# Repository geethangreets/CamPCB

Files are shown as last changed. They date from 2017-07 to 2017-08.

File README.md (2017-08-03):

# Hardware Development of Illumination and Sensor Board for Multispectral Cameras System 
This project is about hardware development for a vital sign detection device

This is a device that allows patients to take images of wounds at their homes with a higher frequency compared to typical hospital visits. The images would then be made available to their clinicians for continuous wound monitoring.

System Diagram:
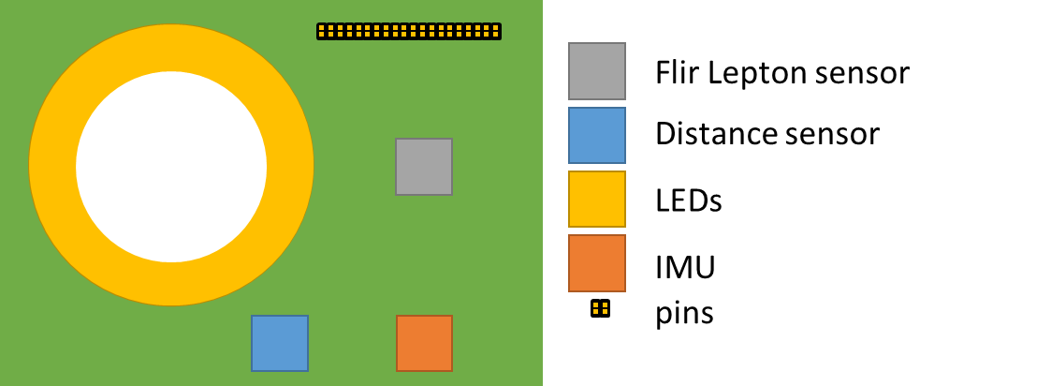
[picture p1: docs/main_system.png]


3D rendering of the assembly:
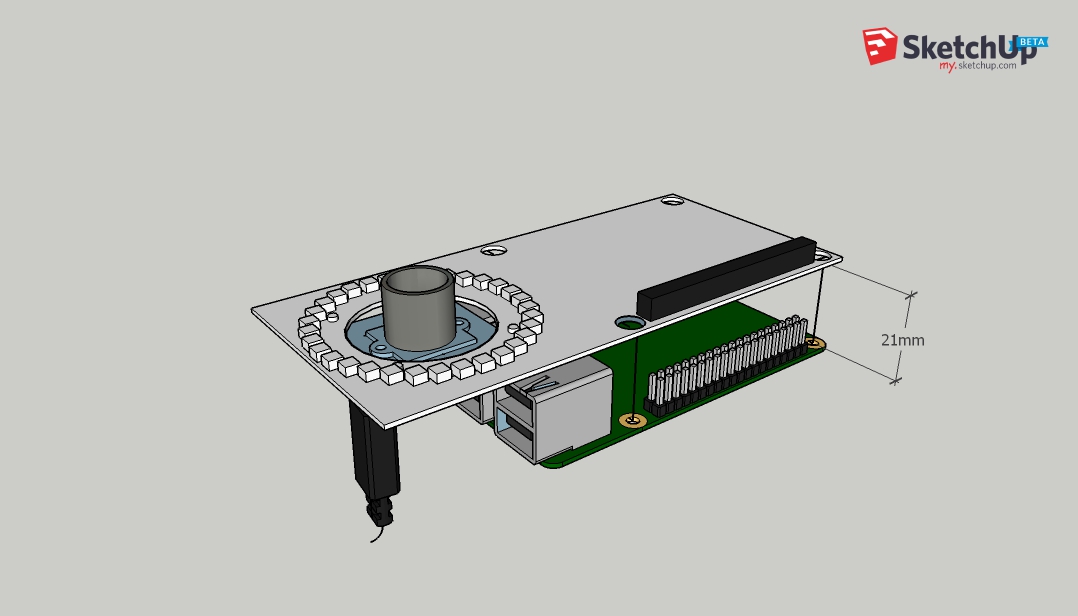
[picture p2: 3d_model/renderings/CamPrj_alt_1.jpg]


Final PCB rendering front and back
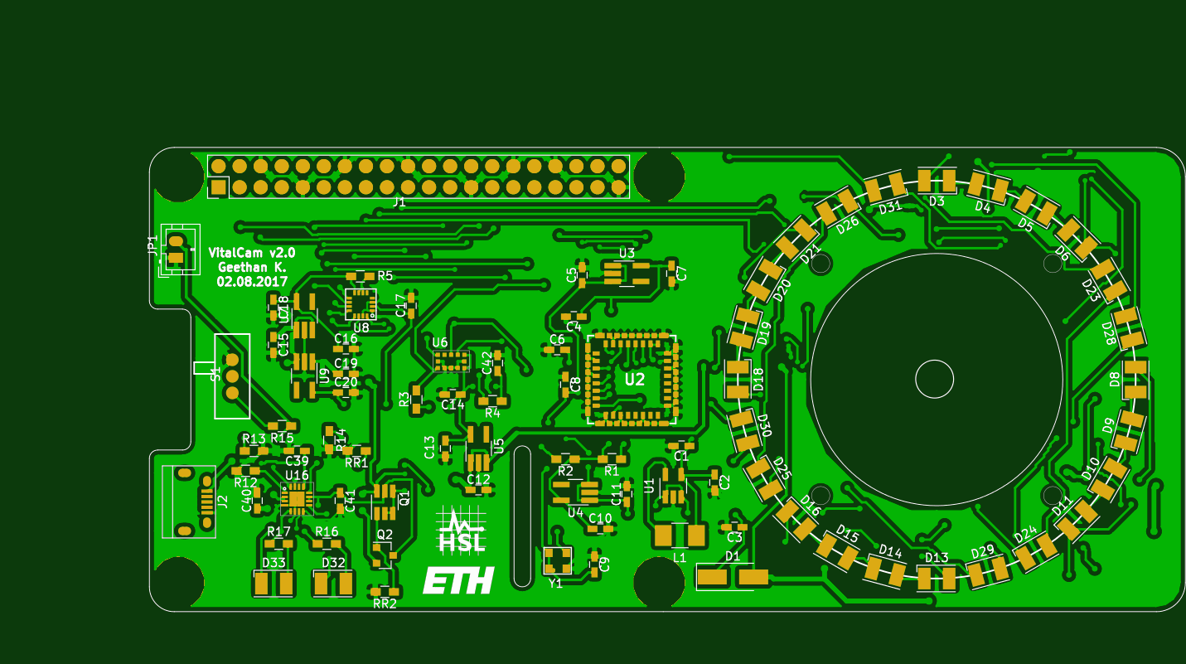
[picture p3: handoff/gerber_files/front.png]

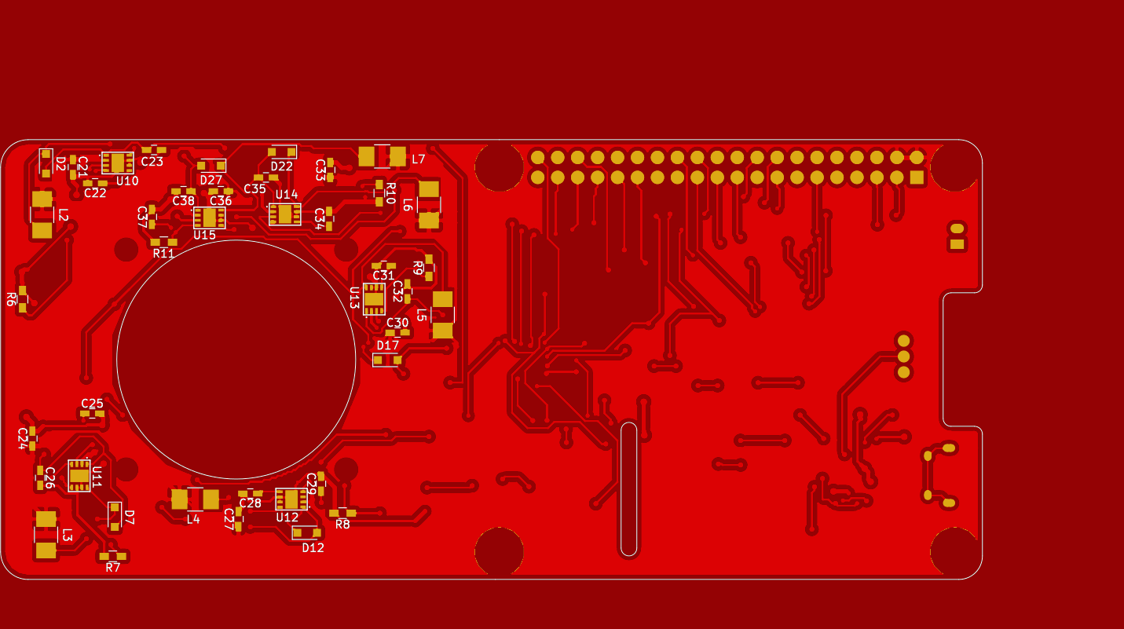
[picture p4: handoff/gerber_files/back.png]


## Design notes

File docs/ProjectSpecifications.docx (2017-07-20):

# Specifications Illumination and sensor board for multispectral cameras system

Author: Gaetano Scebba

Version: V3 (2017-06-02)

1. Motivation

Management and treatment of chronic wounds represent a challenge for both the patients and the medical practitioners. Typically, the wound healing process is slow, so the structural wound changes can be recognized only across several days or weeks. This is why most wound treatments involve weekly visits to the hospital, to document the current wound state. However, in some cases, this low frequency of hospital visits can lead to critical delays in wound interventions in case the wound condition changes more rapidly.

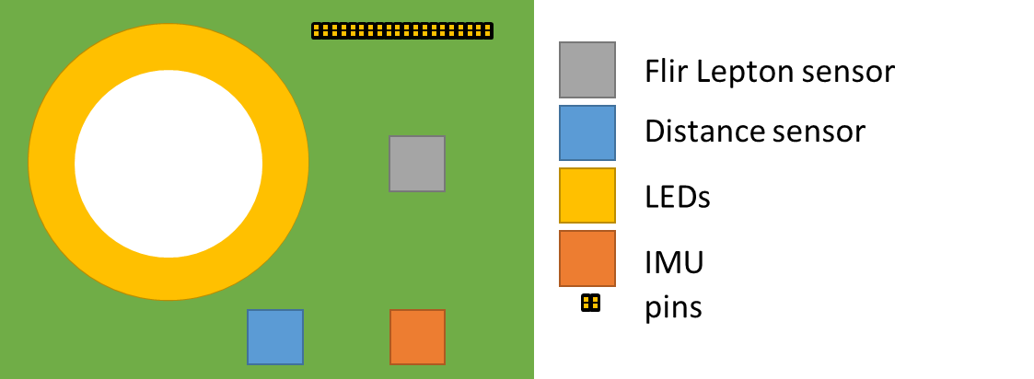
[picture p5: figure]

Our research group is interested in developing a device that allows patients to take images of wounds at their homes with a higher frequency compared to typical hospital visits. The images would then be made available to their clinicians for continuous wound monitoring.

Figure 1 Main components of the designed PCB

2. Purpose

The purpose of this document is to provide specifications for the design and develop of a printed circuit board (PCB) for enhancing a multispectral cameras system (VIS-IR econ systemse-CAM40_CUMI4682_MOD - 4 MP OV4682[^1]) interfaced to a Raspberry PI 3 board. The PCB (Figure 1) will provide following functions:

1. Illumination in infrared, ultraviolet and visible spectrum
2. Thermal (FIR) imaging
3. Distance measurement
4. Spatial orientation measurement
3. PCB specifications

Description | Quantity | Wavelength
SMD Infrared LED | 20 | 850 nm
SMD Ultra-violet LED | 4 | 405 nm
SMD White LED | 4 | -

- The PCB shall integrate the following sets of LEDs:
- The PCB shall integrate all the circuits and mounts for adding and operating the following sensors:
  - Flir Lepton infrared camera sensor;
  - ST’s VL53L0X distance sensor;
  - FIS1100 Inertial Measurement Unit;
- The PCB shall integrate 40 pins (2x20) to be interfaced with the Raspberry PI 3 board.
4. PCB requirements
- The intensity of each set of LEDs shall be individually controllable using continuous current;
- The Flir Lepton sensor shall be fully operational;
- The VL53L0X distance sensor shall be fully operational;

Figure 2 Format and dimensions

- The FIS1100 IMU shall be fully operational.

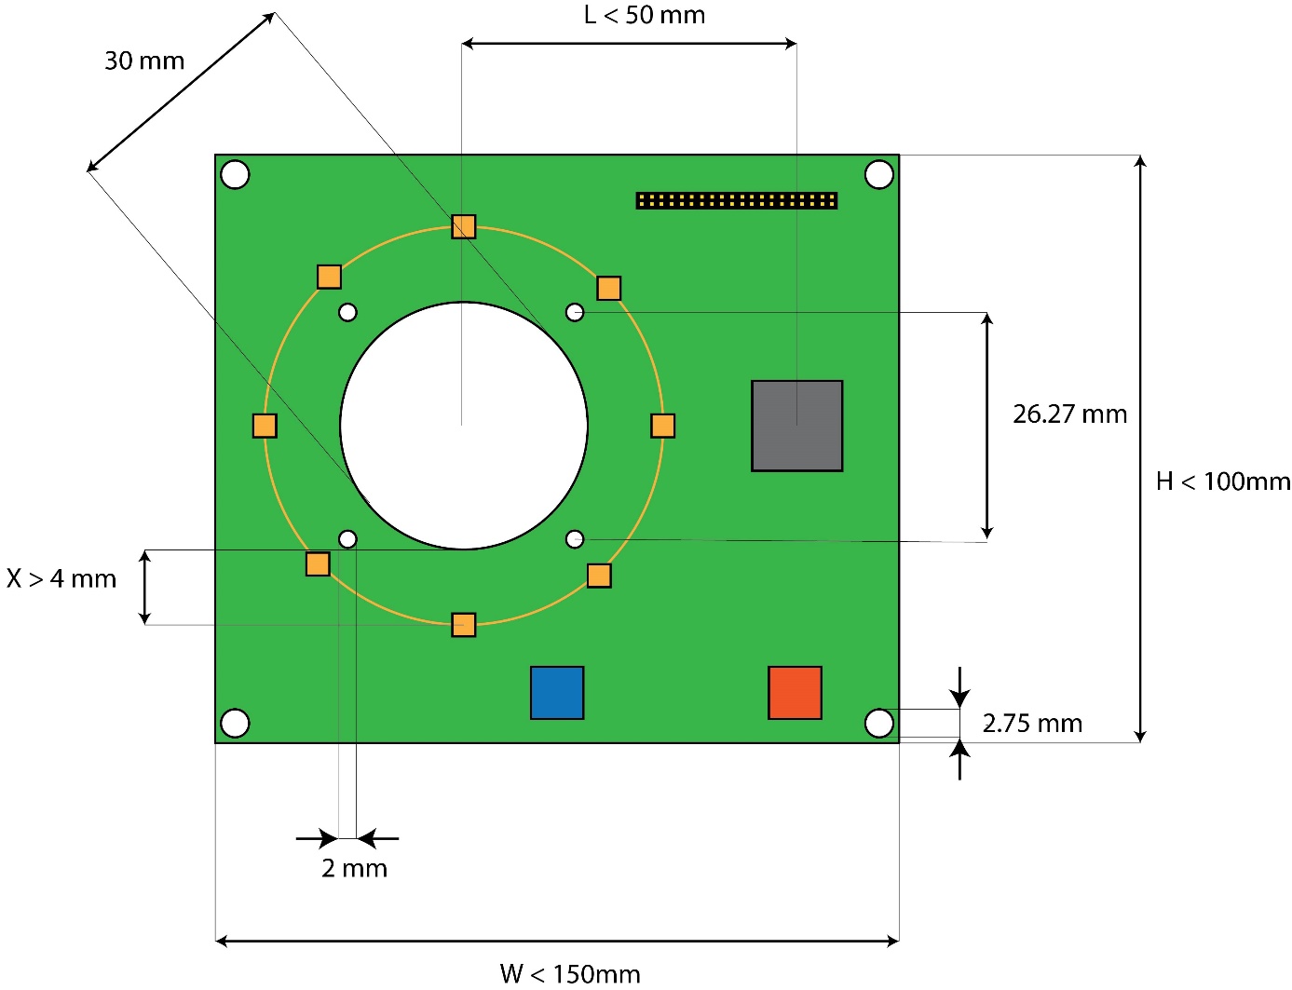
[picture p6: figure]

5. Tasks list
  5.1 Debug the existing PCB prototype;
  5.2 Design of the revised PCB with the desired specifications and requirements;
  5.3 Ordering of the components;
  5.4 PCB manufacturing;
  5.5 Test of the requirements;
  5.6 Documentation and getting-started guide.
6. Milestones
  6.1 Report of the bugs and planned revisions;
  6.2 Pre-manufacturing report of the PCB;
  6.3 Demo of the final system.
7. Further duties

Log worked hours and report weekly.

8. Components
  8.1 Flir Lepton sensor and breakout board

Figure 3 Flir Lepton sensor

Figure 4 Flir Lepton breakout board and Flir Lepton sensor

The Flir Lepton is an infrared camera system that integrates a fixed-focus lens assembly, an 80x60 long-wave infrared microbolometer sensor array, and the signal-processing electronics.

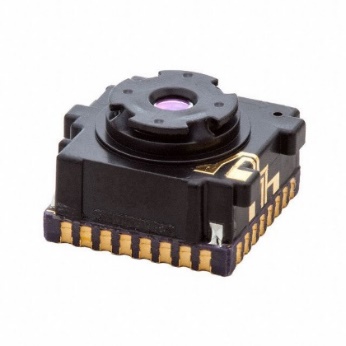
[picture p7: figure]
Image result for flir lepton sensor

The schematic of the operating circuit for the Flir Lepton is in FlirLeptonSensor/LeptonSchematic.pdf

8.2 VL53L0X Time-of Flight distance sensor carrier

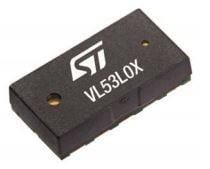
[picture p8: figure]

The VL53L0X is a time-of-flight laser sensor for distance measurement. It can measure absolute distances up to 2 meters.

Figure 4 VL53L0X distance sensor

The schematic of the operating circuit for the VL53L0X distance sensor is in DistanceSensor/DistSchematic.png

8.3 FIS1100 Inertial Measurement Unit

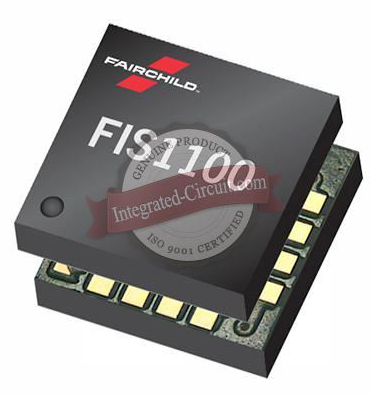
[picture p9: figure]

The FIS1100 is an integrated 6-axis MEMS sensor that includes a 3D accelerometer, a 3D gyroscope and a custom vector digital signal processor.

Figure 5 FIS1100 IMU

The datasheet of the FIS1100 IMU is in IMU/FIS1100Datasheet.pdf

[^1] https://www.e-consystems.com/OV4682-RGB-IR-MIPI-CAMERA-Module.asp

Specifications PCB camera extension board 4/4

Mobile Health Systems Lab

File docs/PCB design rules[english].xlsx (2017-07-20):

Sheet1
 | A | B | C | D
1 | SMS Design Rules (default) | Fat: Accepted by PCB pool (27.11.13) | 29.9.15, Michael Herold-Nadig
2
3 | What? | Values (mm) | Values (mil, obsolete)
4
5 | Minimum ring on Via | 0.2 mm all around | 8 mil all around
6 | Minimal Via (final diameter) | 0.3 mm hole / 0.7 mm pad | 12 mil hole / 28 mil pad | 0.2 mm / 8 mil hole for an extra charge
7 | Signal Via | 0.4 mm hole / 0.9 mm pad | 16 mil hole / 36 mil pad
8th | Larger Via 0.5 mm | 0.6 mm hole / 0.9 mm pad | 24 mil hole / 36 mil pad
9
10
11
12 | Minimum trace | 0.15 mm | 6 mil | 0.125 mm / 5 mil with surcharge
13 | Normal signal trace | 0.3 mm | 12 mils
14 | Normal supply line | 0.6 mm | 24 mil
15 | Main power supply conductor track | 1 mm | 40 mils
16
17
18 | Minimum clearance between conductors | 0.15 mm | 6 mil | 0.125 mm / 5 mil with surcharge
19 | Minimum clearance between hole & Cu | 0.3 mm | 12 mils | Can be guaranteed with a small restring on the inside of 0.15 mm around the circumference.
20 | Min. Distance to PCB outline | 0.2 mm | 8 mils
21
22 | The minimum font size in copper | 0.8 mm height, 0.15 mm line thickness, default font (Stroke) | 32 mil height, 6 mil thickness, default font (Stroke) | Bottom Layer = Mirror!
23 | Normal font size in copper | 1.5 mm height, 0.25 mm thickness, default font (stroke) | 60 mil height, 10 mil thickness, default font (Stroke) | Bottom Layer = Mirror!
24 | The minimum font size to Solder | 1.0 mm Height, 0.15 mm Thickness, Default Font (Stroke) | 40 m height | Under the writing, Cu surface (or even text in Cu) should be, so readable.
25 | Normal font size on Solder | 1.5 mm Height, 0.25 mm Thickness, Default Font (Stroke) | 60 m height | Under the writing, Cu surface (or even text in Cu) should be, so readable.
26
27
28
29
30 | paste mask | 100 μm thick (instead of 120 or 150 μm)
31 | Padreduktion, PasteMaskExpansion (especially with QFP important, otherwise too many shorts due to too much paste) | - 50 μm | - 2 mil

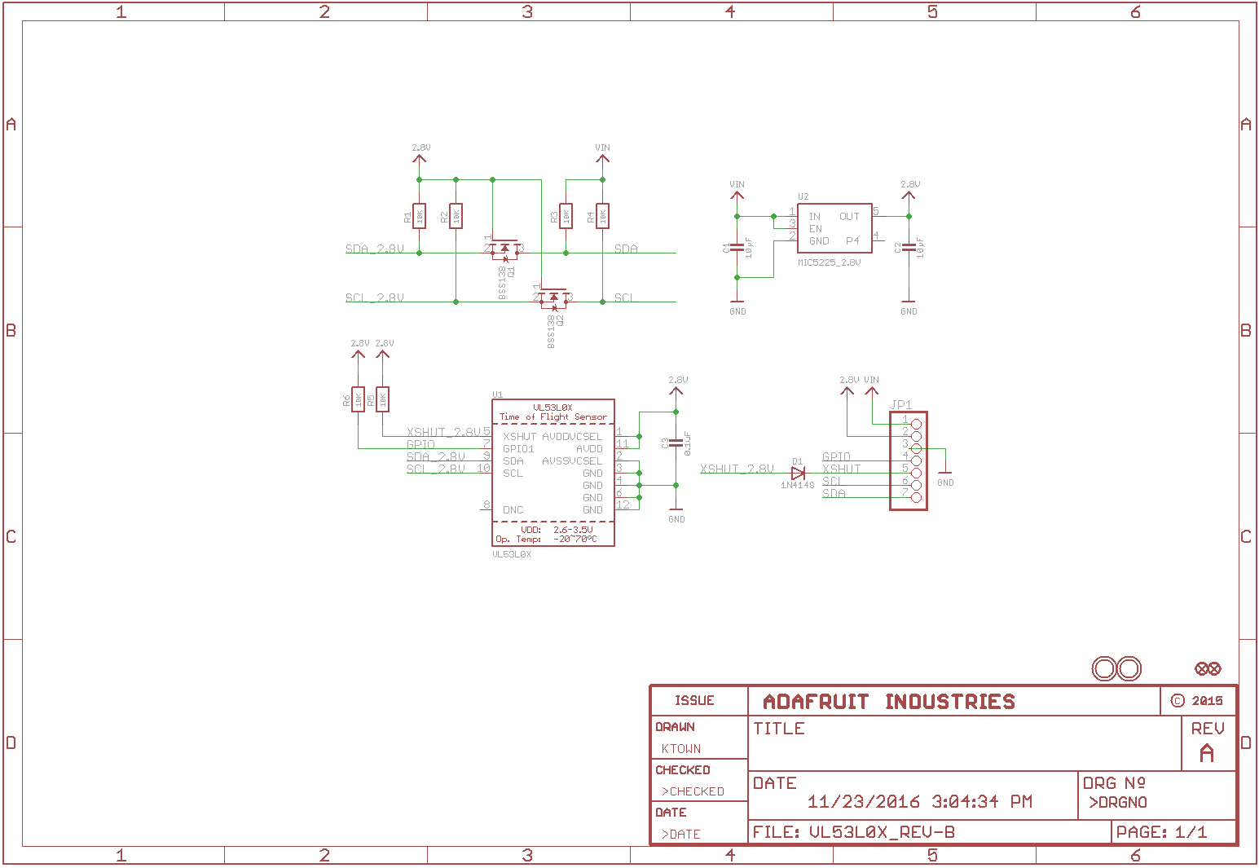
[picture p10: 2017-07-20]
DistanceSensor/DistSchematic.png

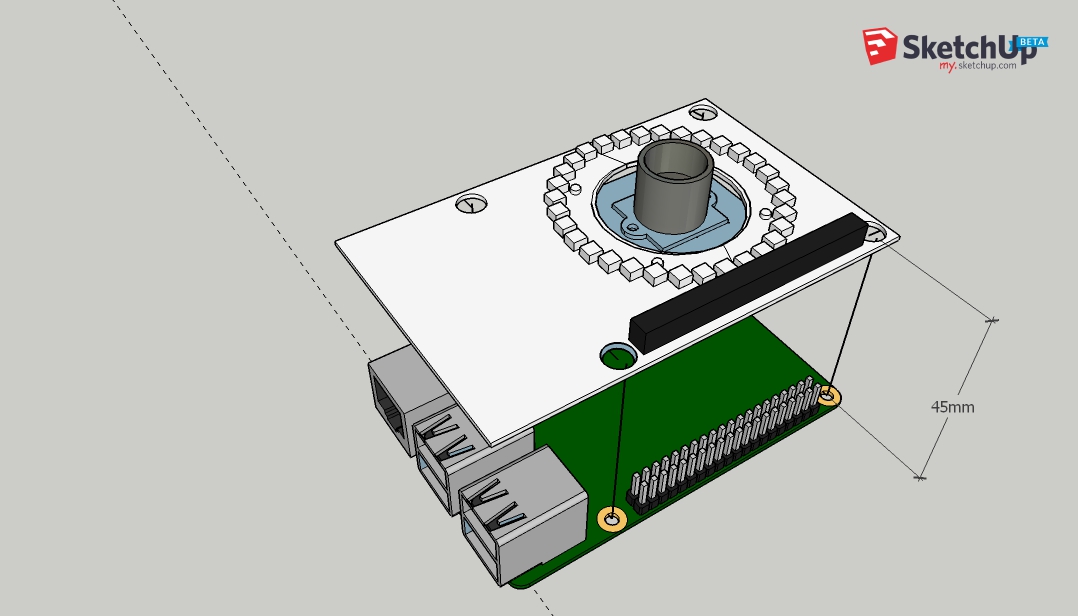
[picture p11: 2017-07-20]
3d_model/renderings/CamPrj_alt_2.jpg

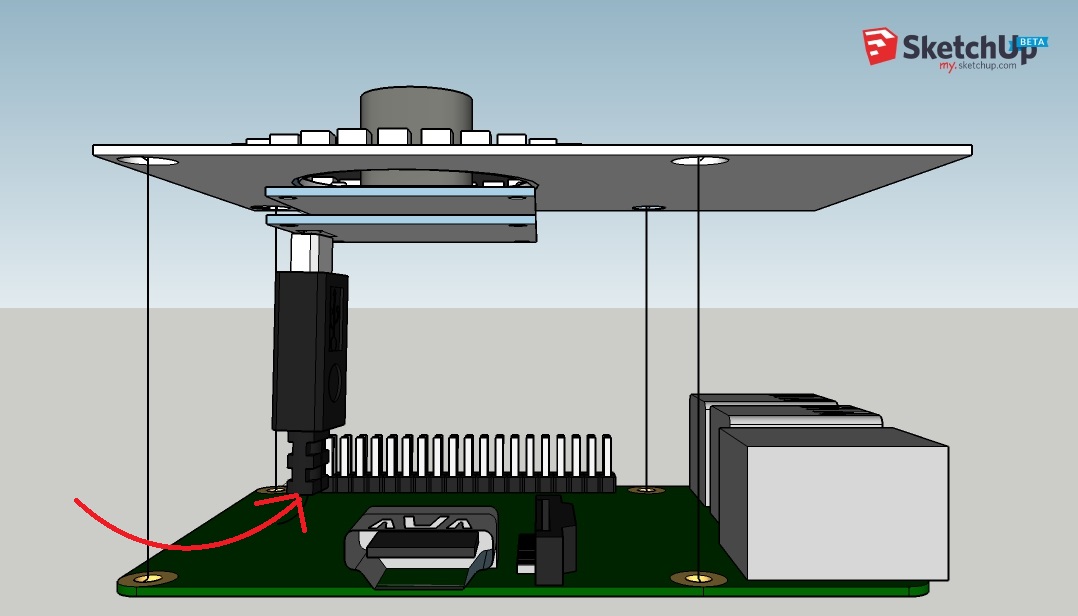
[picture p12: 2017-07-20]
3d_model/renderings/CamPrj_alt_2_access.jpg

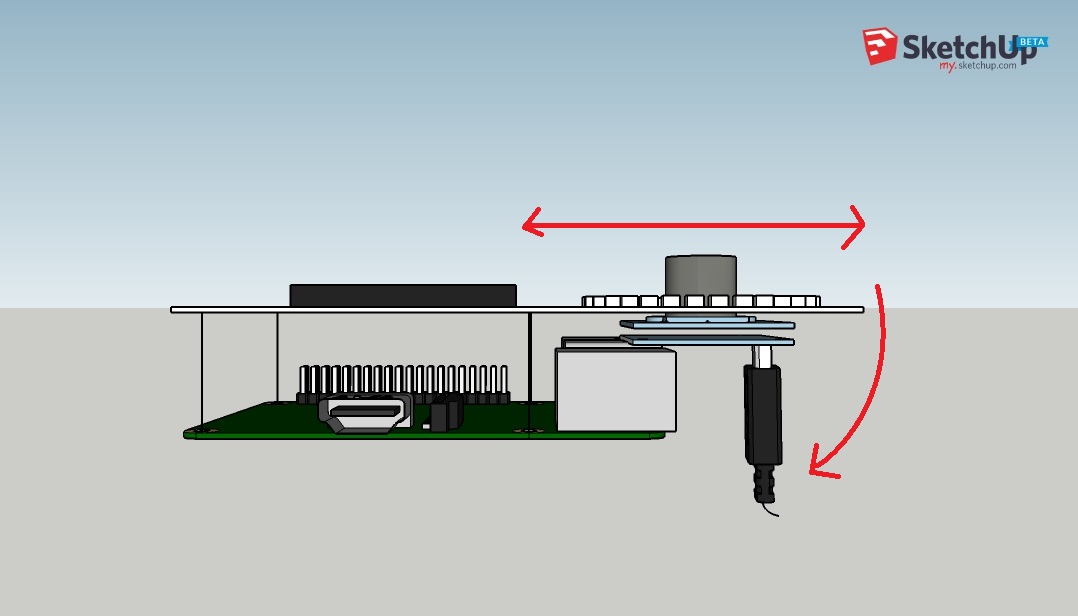
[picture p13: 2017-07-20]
3d_model/renderings/CamPrj_alt_1_stress.jpg

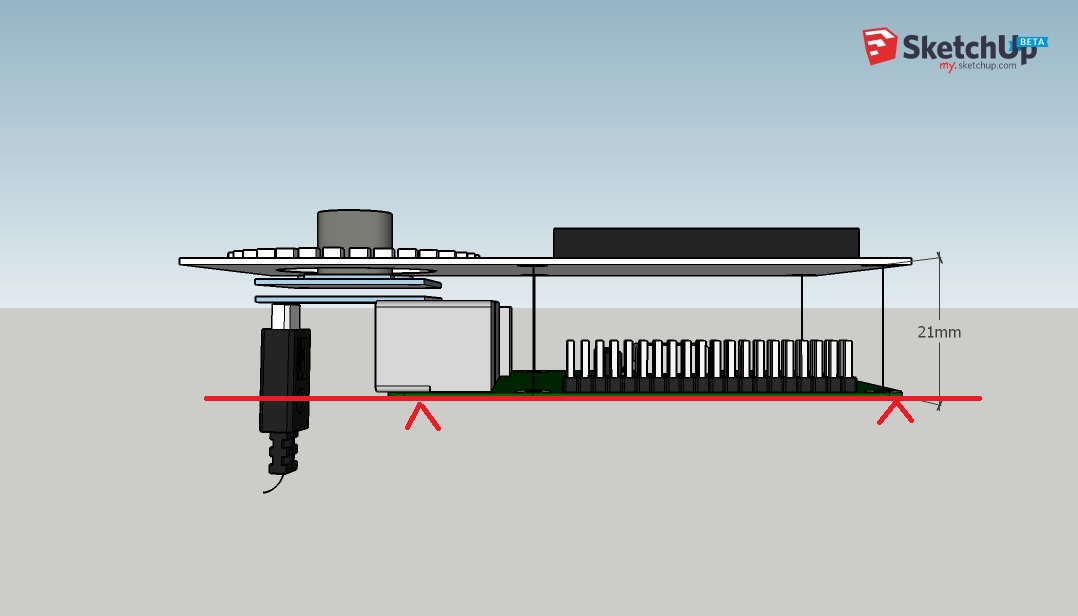
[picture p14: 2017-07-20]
3d_model/renderings/CamPrj_alt_1_usb_obs.jpg

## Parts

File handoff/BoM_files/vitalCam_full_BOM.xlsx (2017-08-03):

version | source | date | tool | number | name | tstamps | title | company | rev | date2 | source3 | number4 | value | ref | value5 | footprint | datasheet | field | name6 | lib | part | names | tstamps7 | tstamp | lib8 | part9 | description | fp | field10 | name11 | num | name12 | type | docs | logical | uri | code | name13 | ref14 | pin
D | E:/ETH/Summer2017/repo/camprj_kicad/camprj_kicad.sch | 8/2/2017 11:28:47 PM | Eeschema 4.0.6 | 1 | / | / |  |  |  | 15 nov 2012 | camprj_kicad.sch | 1
D | E:/ETH/Summer2017/repo/camprj_kicad/camprj_kicad.sch | 8/2/2017 11:28:47 PM | Eeschema 4.0.6 | 1 | / | / |  |  |  | 15 nov 2012 | camprj_kicad.sch | 2
D | E:/ETH/Summer2017/repo/camprj_kicad/camprj_kicad.sch | 8/2/2017 11:28:47 PM | Eeschema 4.0.6 | 1 | / | / |  |  |  | 15 nov 2012 | camprj_kicad.sch | 3
D | E:/ETH/Summer2017/repo/camprj_kicad/camprj_kicad.sch | 8/2/2017 11:28:47 PM | Eeschema 4.0.6 | 1 | / | / |  |  |  | 15 nov 2012 | camprj_kicad.sch | 4
D | E:/ETH/Summer2017/repo/camprj_kicad/camprj_kicad.sch | 8/2/2017 11:28:47 PM | Eeschema 4.0.6 | 2 | /RPI_pinout/ | /595CCA9D/ | Raspberry PI IO subcircuit | MHSL ETH Zurich | 1 | 2017-07-06 | RPI_pinout.sch | 1 | Geethan Karunaratne
D | E:/ETH/Summer2017/repo/camprj_kicad/camprj_kicad.sch | 8/2/2017 11:28:47 PM | Eeschema 4.0.6 | 2 | /RPI_pinout/ | /595CCA9D/ | Raspberry PI IO subcircuit | MHSL ETH Zurich | 1 | 2017-07-06 | RPI_pinout.sch | 2
D | E:/ETH/Summer2017/repo/camprj_kicad/camprj_kicad.sch | 8/2/2017 11:28:47 PM | Eeschema 4.0.6 | 2 | /RPI_pinout/ | /595CCA9D/ | Raspberry PI IO subcircuit | MHSL ETH Zurich | 1 | 2017-07-06 | RPI_pinout.sch | 3
D | E:/ETH/Summer2017/repo/camprj_kicad/camprj_kicad.sch | 8/2/2017 11:28:47 PM | Eeschema 4.0.6 | 2 | /RPI_pinout/ | /595CCA9D/ | Raspberry PI IO subcircuit | MHSL ETH Zurich | 1 | 2017-07-06 | RPI_pinout.sch | 4
D | E:/ETH/Summer2017/repo/camprj_kicad/camprj_kicad.sch | 8/2/2017 11:28:47 PM | Eeschema 4.0.6 | 3 | /thermal_sense/ | /595CCEDA/ | Termal sensor sub circuit | MHSL ETH Zurich | 1 | 2017-07-06 | thermal_sense.sch | 1 | Geethan Karunaratne
D | E:/ETH/Summer2017/repo/camprj_kicad/camprj_kicad.sch | 8/2/2017 11:28:47 PM | Eeschema 4.0.6 | 3 | /thermal_sense/ | /595CCEDA/ | Termal sensor sub circuit | MHSL ETH Zurich | 1 | 2017-07-06 | thermal_sense.sch | 2
D | E:/ETH/Summer2017/repo/camprj_kicad/camprj_kicad.sch | 8/2/2017 11:28:47 PM | Eeschema 4.0.6 | 3 | /thermal_sense/ | /595CCEDA/ | Termal sensor sub circuit | MHSL ETH Zurich | 1 | 2017-07-06 | thermal_sense.sch | 3
D | E:/ETH/Summer2017/repo/camprj_kicad/camprj_kicad.sch | 8/2/2017 11:28:47 PM | Eeschema 4.0.6 | 3 | /thermal_sense/ | /595CCEDA/ | Termal sensor sub circuit | MHSL ETH Zurich | 1 | 2017-07-06 | thermal_sense.sch | 4
D | E:/ETH/Summer2017/repo/camprj_kicad/camprj_kicad.sch | 8/2/2017 11:28:47 PM | Eeschema 4.0.6 | 4 | /dist_sensor/ | /595F7B59/ | Distance Sensor sub circuit | MHSL ETH Zurich | 1 | 2017-07-06 | dist_sensor.sch | 1 | Geethan Karunaratne
D | E:/ETH/Summer2017/repo/camprj_kicad/camprj_kicad.sch | 8/2/2017 11:28:47 PM | Eeschema 4.0.6 | 4 | /dist_sensor/ | /595F7B59/ | Distance Sensor sub circuit | MHSL ETH Zurich | 1 | 2017-07-06 | dist_sensor.sch | 2
D | E:/ETH/Summer2017/repo/camprj_kicad/camprj_kicad.sch | 8/2/2017 11:28:47 PM | Eeschema 4.0.6 | 4 | /dist_sensor/ | /595F7B59/ | Distance Sensor sub circuit | MHSL ETH Zurich | 1 | 2017-07-06 | dist_sensor.sch | 3
D | E:/ETH/Summer2017/repo/camprj_kicad/camprj_kicad.sch | 8/2/2017 11:28:47 PM | Eeschema 4.0.6 | 4 | /dist_sensor/ | /595F7B59/ | Distance Sensor sub circuit | MHSL ETH Zurich | 1 | 2017-07-06 | dist_sensor.sch | 4
D | E:/ETH/Summer2017/repo/camprj_kicad/camprj_kicad.sch | 8/2/2017 11:28:47 PM | Eeschema 4.0.6 | 5 | /IMU/ | /595FA242/ | IMU sub ciruit | MHSL ETH Zurich | 1 | 2017-07-06 | IMU.sch | 1 | Geethan Karunaratne
D | E:/ETH/Summer2017/repo/camprj_kicad/camprj_kicad.sch | 8/2/2017 11:28:47 PM | Eeschema 4.0.6 | 5 | /IMU/ | /595FA242/ | IMU sub ciruit | MHSL ETH Zurich | 1 | 2017-07-06 | IMU.sch | 2
D | E:/ETH/Summer2017/repo/camprj_kicad/camprj_kicad.sch | 8/2/2017 11:28:47 PM | Eeschema 4.0.6 | 5 | /IMU/ | /595FA242/ | IMU sub ciruit | MHSL ETH Zurich | 1 | 2017-07-06 | IMU.sch | 3
D | E:/ETH/Summer2017/repo/camprj_kicad/camprj_kicad.sch | 8/2/2017 11:28:47 PM | Eeschema 4.0.6 | 5 | /IMU/ | /595FA242/ | IMU sub ciruit | MHSL ETH Zurich | 1 | 2017-07-06 | IMU.sch | 4
D | E:/ETH/Summer2017/repo/camprj_kicad/camprj_kicad.sch | 8/2/2017 11:28:47 PM | Eeschema 4.0.6 | 6 | /LED_Drive/ | /59604F02/ |  |  |  |  | LED_Drive.sch | 1
D | E:/ETH/Summer2017/repo/camprj_kicad/camprj_kicad.sch | 8/2/2017 11:28:47 PM | Eeschema 4.0.6 | 6 | /LED_Drive/ | /59604F02/ |  |  |  |  | LED_Drive.sch | 2
D | E:/ETH/Summer2017/repo/camprj_kicad/camprj_kicad.sch | 8/2/2017 11:28:47 PM | Eeschema 4.0.6 | 6 | /LED_Drive/ | /59604F02/ |  |  |  |  | LED_Drive.sch | 3
D | E:/ETH/Summer2017/repo/camprj_kicad/camprj_kicad.sch | 8/2/2017 11:28:47 PM | Eeschema 4.0.6 | 6 | /LED_Drive/ | /59604F02/ |  |  |  |  | LED_Drive.sch | 4
D | E:/ETH/Summer2017/repo/camprj_kicad/camprj_kicad.sch | 8/2/2017 11:28:47 PM | Eeschema 4.0.6 | 7 | /LED_Drive/IR_SET1/ | /59604F02/59604F09/ | LED Driver | MHSL ETH Zurich | 1 | 2017-08-02 | single_led_drive.sch | 1 | Geethan Karunaratne
D | E:/ETH/Summer2017/repo/camprj_kicad/camprj_kicad.sch | 8/2/2017 11:28:47 PM | Eeschema 4.0.6 | 7 | /LED_Drive/IR_SET1/ | /59604F02/59604F09/ | LED Driver | MHSL ETH Zurich | 1 | 2017-08-02 | single_led_drive.sch | 2
D | E:/ETH/Summer2017/repo/camprj_kicad/camprj_kicad.sch | 8/2/2017 11:28:47 PM | Eeschema 4.0.6 | 7 | /LED_Drive/IR_SET1/ | /59604F02/59604F09/ | LED Driver | MHSL ETH Zurich | 1 | 2017-08-02 | single_led_drive.sch | 3
D | E:/ETH/Summer2017/repo/camprj_kicad/camprj_kicad.sch | 8/2/2017 11:28:47 PM | Eeschema 4.0.6 | 7 | /LED_Drive/IR_SET1/ | /59604F02/59604F09/ | LED Driver | MHSL ETH Zurich | 1 | 2017-08-02 | single_led_drive.sch | 4
D | E:/ETH/Summer2017/repo/camprj_kicad/camprj_kicad.sch | 8/2/2017 11:28:47 PM | Eeschema 4.0.6 | 8 | /LED_Drive/IR_SET2/ | /59604F02/59607CD4/ | LED Driver | MHSL ETH Zurich | 1 | 2017-08-02 | single_led_drive.sch | 1 | Geethan Karunaratne
D | E:/ETH/Summer2017/repo/camprj_kicad/camprj_kicad.sch | 8/2/2017 11:28:47 PM | Eeschema 4.0.6 | 8 | /LED_Drive/IR_SET2/ | /59604F02/59607CD4/ | LED Driver | MHSL ETH Zurich | 1 | 2017-08-02 | single_led_drive.sch | 2
D | E:/ETH/Summer2017/repo/camprj_kicad/camprj_kicad.sch | 8/2/2017 11:28:47 PM | Eeschema 4.0.6 | 8 | /LED_Drive/IR_SET2/ | /59604F02/59607CD4/ | LED Driver | MHSL ETH Zurich | 1 | 2017-08-02 | single_led_drive.sch | 3
D | E:/ETH/Summer2017/repo/camprj_kicad/camprj_kicad.sch | 8/2/2017 11:28:47 PM | Eeschema 4.0.6 | 8 | /LED_Drive/IR_SET2/ | /59604F02/59607CD4/ | LED Driver | MHSL ETH Zurich | 1 | 2017-08-02 | single_led_drive.sch | 4
D | E:/ETH/Summer2017/repo/camprj_kicad/camprj_kicad.sch | 8/2/2017 11:28:47 PM | Eeschema 4.0.6 | 9 | /LED_Drive/IR_SET3/ | /59604F02/5960845F/ | LED Driver | MHSL ETH Zurich | 1 | 2017-08-02 | single_led_drive.sch | 1 | Geethan Karunaratne
D | E:/ETH/Summer2017/repo/camprj_kicad/camprj_kicad.sch | 8/2/2017 11:28:47 PM | Eeschema 4.0.6 | 9 | /LED_Drive/IR_SET3/ | /59604F02/5960845F/ | LED Driver | MHSL ETH Zurich | 1 | 2017-08-02 | single_led_drive.sch | 2
D | E:/ETH/Summer2017/repo/camprj_kicad/camprj_kicad.sch | 8/2/2017 11:28:47 PM | Eeschema 4.0.6 | 9 | /LED_Drive/IR_SET3/ | /59604F02/5960845F/ | LED Driver | MHSL ETH Zurich | 1 | 2017-08-02 | single_led_drive.sch | 3
D | E:/ETH/Summer2017/repo/camprj_kicad/camprj_kicad.sch | 8/2/2017 11:28:47 PM | Eeschema 4.0.6 | 9 | /LED_Drive/IR_SET3/ | /59604F02/5960845F/ | LED Driver | MHSL ETH Zurich | 1 | 2017-08-02 | single_led_drive.sch | 4
D | E:/ETH/Summer2017/repo/camprj_kicad/camprj_kicad.sch | 8/2/2017 11:28:47 PM | Eeschema 4.0.6 | 10 | /LED_Drive/IR_SET4/ | /59604F02/59608613/ | LED Driver | MHSL ETH Zurich | 1 | 2017-08-02 | single_led_drive.sch | 1 | Geethan Karunaratne
D | E:/ETH/Summer2017/repo/camprj_kicad/camprj_kicad.sch | 8/2/2017 11:28:47 PM | Eeschema 4.0.6 | 10 | /LED_Drive/IR_SET4/ | /59604F02/59608613/ | LED Driver | MHSL ETH Zurich | 1 | 2017-08-02 | single_led_drive.sch | 2
D | E:/ETH/Summer2017/repo/camprj_kicad/camprj_kicad.sch | 8/2/2017 11:28:47 PM | Eeschema 4.0.6 | 10 | /LED_Drive/IR_SET4/ | /59604F02/59608613/ | LED Driver | MHSL ETH Zurich | 1 | 2017-08-02 | single_led_drive.sch | 3
D | E:/ETH/Summer2017/repo/camprj_kicad/camprj_kicad.sch | 8/2/2017 11:28:47 PM | Eeschema 4.0.6 | 10 | /LED_Drive/IR_SET4/ | /59604F02/59608613/ | LED Driver | MHSL ETH Zurich | 1 | 2017-08-02 | single_led_drive.sch | 4
D | E:/ETH/Summer2017/repo/camprj_kicad/camprj_kicad.sch | 8/2/2017 11:28:47 PM | Eeschema 4.0.6 | 11 | /LED_Drive/WH_SET1/ | /59604F02/59608776/ | LED Driver | MHSL ETH Zurich | 1 | 2017-08-02 | single_led_drive.sch | 1 | Geethan Karunaratne
D | E:/ETH/Summer2017/repo/camprj_kicad/camprj_kicad.sch | 8/2/2017 11:28:47 PM | Eeschema 4.0.6 | 11 | /LED_Drive/WH_SET1/ | /59604F02/59608776/ | LED Driver | MHSL ETH Zurich | 1 | 2017-08-02 | single_led_drive.sch | 2
D | E:/ETH/Summer2017/repo/camprj_kicad/camprj_kicad.sch | 8/2/2017 11:28:47 PM | Eeschema 4.0.6 | 11 | /LED_Drive/WH_SET1/ | /59604F02/59608776/ | LED Driver | MHSL ETH Zurich | 1 | 2017-08-02 | single_led_drive.sch | 3
D | E:/ETH/Summer2017/repo/camprj_kicad/camprj_kicad.sch | 8/2/2017 11:28:47 PM | Eeschema 4.0.6 | 11 | /LED_Drive/WH_SET1/ | /59604F02/59608776/ | LED Driver | MHSL ETH Zurich | 1 | 2017-08-02 | single_led_drive.sch | 4
D | E:/ETH/Summer2017/repo/camprj_kicad/camprj_kicad.sch | 8/2/2017 11:28:47 PM | Eeschema 4.0.6 | 12 | /LED_Drive/UV_SET1/ | /59604F02/59608870/ | LED Driver | MHSL ETH Zurich | 1 | 2017-08-02 | single_led_drive.sch | 1 | Geethan Karunaratne
D | E:/ETH/Summer2017/repo/camprj_kicad/camprj_kicad.sch | 8/2/2017 11:28:47 PM | Eeschema 4.0.6 | 12 | /LED_Drive/UV_SET1/ | /59604F02/59608870/ | LED Driver | MHSL ETH Zurich | 1 | 2017-08-02 | single_led_drive.sch | 2
D | E:/ETH/Summer2017/repo/camprj_kicad/camprj_kicad.sch | 8/2/2017 11:28:47 PM | Eeschema 4.0.6 | 12 | /LED_Drive/UV_SET1/ | /59604F02/59608870/ | LED Driver | MHSL ETH Zurich | 1 | 2017-08-02 | single_led_drive.sch | 3
D | E:/ETH/Summer2017/repo/camprj_kicad/camprj_kicad.sch | 8/2/2017 11:28:47 PM | Eeschema 4.0.6 | 12 | /LED_Drive/UV_SET1/ | /59604F02/59608870/ | LED Driver | MHSL ETH Zurich | 1 | 2017-08-02 | single_led_drive.sch | 4
D | E:/ETH/Summer2017/repo/camprj_kicad/camprj_kicad.sch | 8/2/2017 11:28:47 PM | Eeschema 4.0.6 | 13 | /power_supply/ | /595F39B0/ | USB charging and Power Supply | MHSL ETH Zurich | 1 | 2017-07-07 | power_supply.sch | 1 | Geethan Karunaratne
D | E:/ETH/Summer2017/repo/camprj_kicad/camprj_kicad.sch | 8/2/2017 11:28:47 PM | Eeschema 4.0.6 | 13 | /power_supply/ | /595F39B0/ | USB charging and Power Supply | MHSL ETH Zurich | 1 | 2017-07-07 | power_supply.sch | 2
D | E:/ETH/Summer2017/repo/camprj_kicad/camprj_kicad.sch | 8/2/2017 11:28:47 PM | Eeschema 4.0.6 | 13 | /power_supply/ | /595F39B0/ | USB charging and Power Supply | MHSL ETH Zurich | 1 | 2017-07-07 | power_supply.sch | 3
D | E:/ETH/Summer2017/repo/camprj_kicad/camprj_kicad.sch | 8/2/2017 11:28:47 PM | Eeschema 4.0.6 | 13 | /power_supply/ | /595F39B0/ | USB charging and Power Supply | MHSL ETH Zurich | 1 | 2017-07-07 | power_supply.sch | 4
D |  |  |  |  |  |  |  |  |  |  |  |  |  | J1 | 20x2 header | Pin_Headers:Pin_Header_Straight_2x20_Pitch2.54mm | http://suddendocs.samtec.com/catalog_english/esq_th.pdf | https://www.digikey.com/product-detail/en/ESQ-120-69-G-D-LL/ESQ-120-69-G-D-LL-ND/7098805?WT.z_cid=ref_neda_dkc_buynow | Buy Link | conn | Raspberry_Pi_2_3 | /RPI_pinout/ | /595CCA9D/ | 595CCB8C
D |  |  |  |  |  |  |  |  |  |  |  |  |  | J1 | 20x2 header | Pin_Headers:Pin_Header_Straight_2x20_Pitch2.54mm | http://suddendocs.samtec.com/catalog_english/esq_th.pdf | ESQ-120-69-G-D-LL | MPN | conn | Raspberry_Pi_2_3 | /RPI_pinout/ | /595CCA9D/ | 595CCB8C
D |  |  |  |  |  |  |  |  |  |  |  |  |  | U2 | Molex 1052028-1001 | Myfootprints:105028-1001 | http://www.mouser.com/ds/2/276/1050281001_OTHER_SOCKETS-152362.pdf | http://eu.mouser.com/ProductDetail/Molex/105028-1001/?qs=3OKVfsn1b5DSpyA99lGNjg%3D%3D | Buy Link | leptonBreakoutV4 | LEPTONCUSTOM_CAM-MODULE | /thermal_sense/ | /595CCEDA/ | 595DD16C
D |  |  |  |  |  |  |  |  |  |  |  |  |  | U2 | Molex 1052028-1001 | Myfootprints:105028-1001 | http://www.mouser.com/ds/2/276/1050281001_OTHER_SOCKETS-152362.pdf | 105028-1001 | MPN | leptonBreakoutV4 | LEPTONCUSTOM_CAM-MODULE | /thermal_sense/ | /595CCEDA/ | 595DD16C
D |  |  |  |  |  |  |  |  |  |  |  |  |  | U1 | LM3670SOT23-5 | TO_SOT_Packages_SMD:SOT-23-5_HandSoldering | http://www.ti.com/lit/ds/symlink/lm3670.pdf | http://eu.mouser.com/ProductDetail/Texas-Instruments/LM3670MFX-ADJ-NOPB/ | Buy Link | leptonBreakoutV4 | LEPTONCUSTOM_LM3670SOT23-5 | /thermal_sense/ | /595CCEDA/ | 595DD218
D |  |  |  |  |  |  |  |  |  |  |  |  |  | U1 | LM3670SOT23-5 | TO_SOT_Packages_SMD:SOT-23-5_HandSoldering | http://www.ti.com/lit/ds/symlink/lm3670.pdf | LM3670MFX-ADJ/NOPB | MPN | leptonBreakoutV4 | LEPTONCUSTOM_LM3670SOT23-5 | /thermal_sense/ | /595CCEDA/ | 595DD218
D |  |  |  |  |  |  |  |  |  |  |  |  |  | C1 | 10uF | Capacitors_SMD:C_0603_HandSoldering |  |  |  | device | C | /thermal_sense/ | /595CCEDA/ | 595DD448
D |  |  |  |  |  |  |  |  |  |  |  |  |  | L1 | 10uH | Inductors_SMD:L_1210_HandSoldering |  |  |  | device | L | /thermal_sense/ | /595CCEDA/ | 595DD4BD
D |  |  |  |  |  |  |  |  |  |  |  |  |  | C2 | 0.1uF | Capacitors_SMD:C_0603_HandSoldering |  |  |  | device | C | /thermal_sense/ | /595CCEDA/ | 595DD57E
D |  |  |  |  |  |  |  |  |  |  |  |  |  | Y1 | ASFLMB-25MHZ | Myfootprints:5X3.2-CRYSTAL | http://www.mouser.com/ds/2/3/ASFLMB-24525.pdf | http://eu.mouser.com/ProductDetail/ABRACON/ASFLMB-25000MHZ-LC-T/?qs=3YAjQa1E1OmYZx%252blyx8lOg%3D%3D | Buy Link | leptonBreakoutV4 | LEPTONCUSTOM_ASFLMB-25MHZ | /thermal_sense/ | /595CCEDA/ | 595DE58B
D |  |  |  |  |  |  |  |  |  |  |  |  |  | Y1 | ASFLMB-25MHZ | Myfootprints:5X3.2-CRYSTAL | http://www.mouser.com/ds/2/3/ASFLMB-24525.pdf | ASFLMB-25.000MHZ-LC-T | MPN | leptonBreakoutV4 | LEPTONCUSTOM_ASFLMB-25MHZ | /thermal_sense/ | /595CCEDA/ | 595DE58B
D |  |  |  |  |  |  |  |  |  |  |  |  |  | C9 | 10nF | Capacitors_SMD:C_0603_HandSoldering |  |  |  | device | C | /thermal_sense/ | /595CCEDA/ | 595DE822
D |  |  |  |  |  |  |  |  |  |  |  |  |  | R1 | 10K | Resistors_SMD:R_0603_HandSoldering |  |  |  | device | R | /thermal_sense/ | /595CCEDA/ | 595DEE4C
D |  |  |  |  |  |  |  |  |  |  |  |  |  | R2 | 100K | Resistors_SMD:R_0603_HandSoldering |  |  |  | device | R | /thermal_sense/ | /595CCEDA/ | 595DEEFC
D |  |  |  |  |  |  |  |  |  |  |  |  |  | C8 | 1uF | Capacitors_SMD:C_0603_HandSoldering |  |  |  | device | C | /thermal_sense/ | /595CCEDA/ | 595DFC4E
D |  |  |  |  |  |  |  |  |  |  |  |  |  | C6 | 0.1uF | Capacitors_SMD:C_0603_HandSoldering |  |  |  | device | C | /thermal_sense/ | /595CCEDA/ | 595DFD7F
D |  |  |  |  |  |  |  |  |  |  |  |  |  | U4 | ADP150AUJZ-2.8-R7 | TO_SOT_Packages_SMD:TSOT-23-5_HandSoldering | http://www.mouser.com/ds/2/609/ADP150-773560.pdf | http://eu.mouser.com/ProductDetail/Analog-Devices/ADP150AUJZ-28-R7/?qs=WIvQP4zGanh7WlpvNfrmXw%3D%3D | Buy Link | leptonBreakoutV4 | LEPTONCUSTOM_ADP150TSOT-5 | /thermal_sense/ | /595CCEDA/ | 595E0F8D
D |  |  |  |  |  |  |  |  |  |  |  |  |  | U4 | ADP150AUJZ-2.8-R7 | TO_SOT_Packages_SMD:TSOT-23-5_HandSoldering | http://www.mouser.com/ds/2/609/ADP150-773560.pdf | ADP150AUJZ-2.8-R7 | MPN | leptonBreakoutV4 | LEPTONCUSTOM_ADP150TSOT-5 | /thermal_sense/ | /595CCEDA/ | 595E0F8D
D |  |  |  |  |  |  |  |  |  |  |  |  |  | C10 | 1uF | Capacitors_SMD:C_0603_HandSoldering |  |  |  | device | C | /thermal_sense/ | /595CCEDA/ | 595E1253
D |  |  |  |  |  |  |  |  |  |  |  |  |  | C11 | 1uF | Capacitors_SMD:C_0603_HandSoldering |  |  |  | device | C | /thermal_sense/ | /595CCEDA/ | 595E224B
D |  |  |  |  |  |  |  |  |  |  |  |  |  | U3 | ADP150AUJZ-3.3-R7 | TO_SOT_Packages_SMD:TSOT-23-5_HandSoldering | http://www.mouser.com/ds/2/609/ADP150-773560.pdf | http://eu.mouser.com/ProductDetail/Analog-Devices/ADP150AUJZ-33-R7/?qs=WIvQP4zGanjNlX1MqHWsFA%3D%3D | Buy Link | leptonBreakoutV4 | LEPTONCUSTOM_ADP150TSOT-5 | /thermal_sense/ | /595CCEDA/ | 595E2ECE
D |  |  |  |  |  |  |  |  |  |  |  |  |  | U3 | ADP150AUJZ-3.3-R7 | TO_SOT_Packages_SMD:TSOT-23-5_HandSoldering | http://www.mouser.com/ds/2/609/ADP150-773560.pdf | ADP150AUJZ-3.3-R7 | MPN | leptonBreakoutV4 | LEPTONCUSTOM_ADP150TSOT-5 | /thermal_sense/ | /595CCEDA/ | 595E2ECE
D |  |  |  |  |  |  |  |  |  |  |  |  |  | C5 | 1uF | Capacitors_SMD:C_0603_HandSoldering |  |  |  | device | C | /thermal_sense/ | /595CCEDA/ | 595E31FF
D |  |  |  |  |  |  |  |  |  |  |  |  |  | C7 | 1uF | Capacitors_SMD:C_0603_HandSoldering |  |  |  | device | C | /thermal_sense/ | /595CCEDA/ | 595E3957
D |  |  |  |  |  |  |  |  |  |  |  |  |  | C4 | 0.1uF | Capacitors_SMD:C_0603_HandSoldering |  |  |  | device | C | /thermal_sense/ | /595CCEDA/ | 595E6083
D |  |  |  |  |  |  |  |  |  |  |  |  |  | C3 | 4.7uF | Capacitors_SMD:C_0603_HandSoldering |  |  |  | device | C | /thermal_sense/ | /595CCEDA/ | 595E8002
D |  |  |  |  |  |  |  |  |  |  |  |  |  | D1 | B340A | Myfootprints:D_SMA_Handsoldering_AC | http://www.mouser.com/ds/2/115/ds30891-89887.pdf | http://www.mouser.ch/ProductDetail/Diodes-Incorporated/B340A-13-F/?qs=aLaTXeBcTP9fj%2fYKVo6Q1A== | Buy Link | leptonBreakoutV4 | SCHOTTKY-B340A | /thermal_sense/ | /595CCEDA/ | 5974B1F1
D |  |  |  |  |  |  |  |  |  |  |  |  |  | D1 | B340A | Myfootprints:D_SMA_Handsoldering_AC | http://www.mouser.com/ds/2/115/ds30891-89887.pdf | B340A-13-F | MPN | leptonBreakoutV4 | SCHOTTKY-B340A | /thermal_sense/ | /595CCEDA/ | 5974B1F1
D |  |  |  |  |  |  |  |  |  |  |  |  |  | U6 | VL53L0X | Myfootprints:Optical_LGA12 | http://www.mouser.com/ds/2/389/en.DM00279086-952611.pdf | http://eu.mouser.com/ProductDetail/STMicroelectronics/VL53L0CXV0DH-1/?qs=dTJS0cRn7ojtsK3C9%252bTaSw%3d%3d | Buy Link | _sensors | VL53L0X | /dist_sensor/ | /595F7B59/ | 595F7B68
D |  |  |  |  |  |  |  |  |  |  |  |  |  | U6 | VL53L0X | Myfootprints:Optical_LGA12 | http://www.mouser.com/ds/2/389/en.DM00279086-952611.pdf | VL53L0CXV0DH/1 | MPN | _sensors | VL53L0X | /dist_sensor/ | /595F7B59/ | 595F7B68
D |  |  |  |  |  |  |  |  |  |  |  |  |  | R4 | 10K | Resistors_SMD:R_0603_HandSoldering |  |  |  | device | R | /dist_sensor/ | /595F7B59/ | 595F7CD2
D |  |  |  |  |  |  |  |  |  |  |  |  |  | R3 | 10K | Resistors_SMD:R_0603_HandSoldering |  |  |  | device | R | /dist_sensor/ | /595F7B59/ | 595F7D0D
D |  |  |  |  |  |  |  |  |  |  |  |  |  | U5 | ADP150AUJZ-3.3-R7 | TO_SOT_Packages_SMD:TSOT-23-5_HandSoldering | http://www.mouser.com/ds/2/609/ADP150-773560.pdf | http://eu.mouser.com/ProductDetail/Analog-Devices/ADP150AUJZ-33-R7/?qs=WIvQP4zGanjNlX1MqHWsFA%3D%3D | Buy Link | leptonBreakoutV4 | LEPTONCUSTOM_ADP150TSOT-5 | /dist_sensor/ | /595F7B59/ | 595F8383
D |  |  |  |  |  |  |  |  |  |  |  |  |  | U5 | ADP150AUJZ-3.3-R7 | TO_SOT_Packages_SMD:TSOT-23-5_HandSoldering | http://www.mouser.com/ds/2/609/ADP150-773560.pdf | ADP150AUJZ-3.3-R7 | MPN | leptonBreakoutV4 | LEPTONCUSTOM_ADP150TSOT-5 | /dist_sensor/ | /595F7B59/ | 595F8383
D |  |  |  |  |  |  |  |  |  |  |  |  |  | C13 | 10uF | Capacitors_SMD:C_0603_HandSoldering |  |  |  | device | C | /dist_sensor/ | /595F7B59/ | 595F879F
D |  |  |  |  |  |  |  |  |  |  |  |  |  | C12 | 10uF | Capacitors_SMD:C_0603_HandSoldering |  |  |  | device | C | /dist_sensor/ | /595F7B59/ | 595F8DF4
D |  |  |  |  |  |  |  |  |  |  |  |  |  | C14 | 4.7u | Capacitors_SMD:C_0603_HandSoldering |  |  |  | device | C | /dist_sensor/ | /595F7B59/ | 595F9601
D |  |  |  |  |  |  |  |  |  |  |  |  |  | C42 | 100n | Capacitors_SMD:C_0603_HandSoldering |  |  |  | device | C | /dist_sensor/ | /595F7B59/ | 59657C20
D |  |  |  |  |  |  |  |  |  |  |  |  |  | U8 | FIS1100 | Myfootprints:LGA16 | http://www.mouser.com/ds/2/308/FIS1100-1119815.pdf | http://eu.mouser.com/ProductDetail/Fairchild-Semiconductor/FIS1100/?qs=Pve5fMu%2FDEuZUDX%2Fo6J%252b1g%3D%3D | Buy Link | mynew_lib | FIS1100 | /IMU/ | /595FA242/ | 595FAAF9
D |  |  |  |  |  |  |  |  |  |  |  |  |  | U8 | FIS1100 | Myfootprints:LGA16 | http://www.mouser.com/ds/2/308/FIS1100-1119815.pdf | FIS1100 | MPN | mynew_lib | FIS1100 | /IMU/ | /595FA242/ | 595FAAF9
D |  |  |  |  |  |  |  |  |  |  |  |  |  | C16 | 100nF | Capacitors_SMD:C_0603_HandSoldering |  |  |  | device | C | /IMU/ | /595FA242/ | 595FABCD
D |  |  |  |  |  |  |  |  |  |  |  |  |  | U7 | ADP150AUJZ-3.3-R7 | TO_SOT_Packages_SMD:TSOT-23-5_HandSoldering | http://www.mouser.com/ds/2/609/ADP150-773560.pdf | http://eu.mouser.com/ProductDetail/Analog-Devices/ADP150AUJZ-33-R7/?qs=WIvQP4zGanjNlX1MqHWsFA%3D%3D | Buy Link | leptonBreakoutV4 | LEPTONCUSTOM_ADP150TSOT-5 | /IMU/ | /595FA242/ | 595FC827
D |  |  |  |  |  |  |  |  |  |  |  |  |  | U7 | ADP150AUJZ-3.3-R7 | TO_SOT_Packages_SMD:TSOT-23-5_HandSoldering | http://www.mouser.com/ds/2/609/ADP150-773560.pdf | ADP150AUJZ-3.3-R7 | MPN | leptonBreakoutV4 | LEPTONCUSTOM_ADP150TSOT-5 | /IMU/ | /595FA242/ | 595FC827
D |  |  |  |  |  |  |  |  |  |  |  |  |  | C15 | 1uF | Capacitors_SMD:C_0603_HandSoldering |  |  |  | device | C | /IMU/ | /595FA242/ | 595FC82E
D |  |  |  |  |  |  |  |  |  |  |  |  |  | C18 | 1uF | Capacitors_SMD:C_0603_HandSoldering |  |  |  | device | C | /IMU/ | /595FA242/ | 595FC83B
D |  |  |  |  |  |  |  |  |  |  |  |  |  | U9 | ADP150AUJZ-1.8-R7 | TO_SOT_Packages_SMD:TSOT-23-5_HandSoldering | http://www.mouser.com/ds/2/609/ADP150-773560.pdf | http://eu.mouser.com/ProductDetail/Analog-Devices/ADP150AUJZ-18-R7/?qs=WIvQP4zGanj6me7Xqf%252bL8w%3D%3D | Buy Link | leptonBreakoutV4 | LEPTONCUSTOM_ADP150TSOT-5 | /IMU/ | /595FA242/ | 595FCBB7
D |  |  |  |  |  |  |  |  |  |  |  |  |  | U9 | ADP150AUJZ-1.8-R7 | TO_SOT_Packages_SMD:TSOT-23-5_HandSoldering | http://www.mouser.com/ds/2/609/ADP150-773560.pdf | ADP150AUJZ-1.8-R7 | MPN | leptonBreakoutV4 | LEPTONCUSTOM_ADP150TSOT-5 | /IMU/ | /595FA242/ | 595FCBB7
D |  |  |  |  |  |  |  |  |  |  |  |  |  | C19 | 1uF | Capacitors_SMD:C_0603_HandSoldering |  |  |  | device | C | /IMU/ | /595FA242/ | 595FCBBE
D |  |  |  |  |  |  |  |  |  |  |  |  |  | C20 | 1uF | Capacitors_SMD:C_0603_HandSoldering |  |  |  | device | C | /IMU/ | /595FA242/ | 595FCBCB
D |  |  |  |  |  |  |  |  |  |  |  |  |  | C17 | 100nF | Capacitors_SMD:C_0603_HandSoldering |  |  |  | device | C | /IMU/ | /595FA242/ | 595FD69A
D |  |  |  |  |  |  |  |  |  |  |  |  |  | R5 | 10K | Resistors_SMD:R_0603_HandSoldering |  |  |  | device | R | /IMU/ | /595FA242/ | 595FE3A0
D |  |  |  |  |  |  |  |  |  |  |  |  |  | U10 | MAX1561 | SparkFun-PowerIC:8-TDFN-EP | http://www.mouser.com/ds/2/256/MAX1561-MAX1599-65829.pdf | http://www.mouser.ch/ProductDetail/Maxim-Integrated/MAX1561ETA+T/?qs=p6VZ%252bklCkRSw1RT%2f%2fPr34Q== | Buy Link | MAX1599 | MAX1599 | /LED_Drive/IR_SET1/ | /59604F02/59604F09/ | 59604F14
D |  |  |  |  |  |  |  |  |  |  |  |  |  | U10 | MAX1561 | SparkFun-PowerIC:8-TDFN-EP | http://www.mouser.com/ds/2/256/MAX1561-MAX1599-65829.pdf | MAX1561ETA+T | MPN | MAX1599 | MAX1599 | /LED_Drive/IR_SET1/ | /59604F02/59604F09/ | 59604F14
D |  |  |  |  |  |  |  |  |  |  |  |  |  | C22 | 0.1uF | Capacitors_SMD:C_0603_HandSoldering |  |  |  | device | C | /LED_Drive/IR_SET1/ | /59604F02/59604F09/ | 5960555F
D |  |  |  |  |  |  |  |  |  |  |  |  |  | C21 | 2.2uF | Capacitors_SMD:C_0603_HandSoldering |  |  |  | device | C | /LED_Drive/IR_SET1/ | /59604F02/59604F09/ | 5960566F
D |  |  |  |  |  |  |  |  |  |  |  |  |  | C23 | 0.1uF | Capacitors_SMD:C_0603_HandSoldering |  |  |  | device | C | /LED_Drive/IR_SET1/ | /59604F02/59604F09/ | 5960587B
D |  |  |  |  |  |  |  |  |  |  |  |  |  | L2 | 47uH | Inductors_SMD:L_1210_HandSoldering |  |  |  | device | L | /LED_Drive/IR_SET1/ | /59604F02/59604F09/ | 59605DEA
D |  |  |  |  |  |  |  |  |  |  |  |  |  | D3 | LED | LEDs:LED_PLCC-2 |  |  |  | device | LED | /LED_Drive/IR_SET1/ | /59604F02/59604F09/ | 59606309
D |  |  |  |  |  |  |  |  |  |  |  |  |  | D4 | LED | LEDs:LED_PLCC-2 |  |  |  | device | LED | /LED_Drive/IR_SET1/ | /59604F02/59604F09/ | 596063DB
D |  |  |  |  |  |  |  |  |  |  |  |  |  | D5 | LED | LEDs:LED_PLCC-2 |  |  |  | device | LED | /LED_Drive/IR_SET1/ | /59604F02/59604F09/ | 596064A1
D |  |  |  |  |  |  |  |  |  |  |  |  |  | D6 | LED | LEDs:LED_PLCC-2 |  |  |  | device | LED | /LED_Drive/IR_SET1/ | /59604F02/59604F09/ | 596064D7
D |  |  |  |  |  |  |  |  |  |  |  |  |  | R6 | 7.5 | Resistors_SMD:R_0603_HandSoldering |  |  |  | device | R | /LED_Drive/IR_SET1/ | /59604F02/59604F09/ | 59606544
D |  |  |  |  |  |  |  |  |  |  |  |  |  | D2 | CMDSH2-3 | Diodes_SMD:D_SOD-323_HandSoldering | http://www.mouser.com/ds/2/68/cmdsh2-3-39086.pdf | http://www.mouser.ch/ProductDetail/Central-Semiconductor/CMDSH2-3-TR/?qs=AjE1biBnhWMUdOF9vZ5x%252bg== | Buy Link | mynew_lib | CMDSH2-3 | /LED_Drive/IR_SET1/ | /59604F02/59604F09/ | 597479DB
D |  |  |  |  |  |  |  |  |  |  |  |  |  | D2 | CMDSH2-3 | Diodes_SMD:D_SOD-323_HandSoldering | http://www.mouser.com/ds/2/68/cmdsh2-3-39086.pdf | CMDSH2-3 TR | MPN | mynew_lib | CMDSH2-3 | /LED_Drive/IR_SET1/ | /59604F02/59604F09/ | 597479DB
D |  |  |  |  |  |  |  |  |  |  |  |  |  | U11 | MAX1561 | SparkFun-PowerIC:8-TDFN-EP | http://www.mouser.com/ds/2/256/MAX1561-MAX1599-65829.pdf | http://www.mouser.ch/ProductDetail/Maxim-Integrated/MAX1561ETA+T/?qs=p6VZ%252bklCkRSw1RT%2f%2fPr34Q== | Buy Link | MAX1599 | MAX1599 | /LED_Drive/IR_SET2/ | /59604F02/59607CD4/ | 59604F14
D |  |  |  |  |  |  |  |  |  |  |  |  |  | U11 | MAX1561 | SparkFun-PowerIC:8-TDFN-EP | http://www.mouser.com/ds/2/256/MAX1561-MAX1599-65829.pdf | MAX1561ETA+T | MPN | MAX1599 | MAX1599 | /LED_Drive/IR_SET2/ | /59604F02/59607CD4/ | 59604F14
D |  |  |  |  |  |  |  |  |  |  |  |  |  | C25 | 0.1uF | Capacitors_SMD:C_0603_HandSoldering |  |  |  | device | C | /LED_Drive/IR_SET2/ | /59604F02/59607CD4/ | 5960555F
D |  |  |  |  |  |  |  |  |  |  |  |  |  | C24 | 2.2uF | Capacitors_SMD:C_0603_HandSoldering |  |  |  | device | C | /LED_Drive/IR_SET2/ | /59604F02/59607CD4/ | 5960566F
D |  |  |  |  |  |  |  |  |  |  |  |  |  | C26 | 0.1uF | Capacitors_SMD:C_0603_HandSoldering |  |  |  | device | C | /LED_Drive/IR_SET2/ | /59604F02/59607CD4/ | 5960587B
D |  |  |  |  |  |  |  |  |  |  |  |  |  | L3 | 47uH | Inductors_SMD:L_1210_HandSoldering |  |  |  | device | L | /LED_Drive/IR_SET2/ | /59604F02/59607CD4/ | 59605DEA
D |  |  |  |  |  |  |  |  |  |  |  |  |  | D8 | LED | LEDs:LED_PLCC-2 |  |  |  | device | LED | /LED_Drive/IR_SET2/ | /59604F02/59607CD4/ | 59606309
D |  |  |  |  |  |  |  |  |  |  |  |  |  | D9 | LED | LEDs:LED_PLCC-2 |  |  |  | device | LED | /LED_Drive/IR_SET2/ | /59604F02/59607CD4/ | 596063DB
D |  |  |  |  |  |  |  |  |  |  |  |  |  | D10 | LED | LEDs:LED_PLCC-2 |  |  |  | device | LED | /LED_Drive/IR_SET2/ | /59604F02/59607CD4/ | 596064A1
D |  |  |  |  |  |  |  |  |  |  |  |  |  | D11 | LED | LEDs:LED_PLCC-2 |  |  |  | device | LED | /LED_Drive/IR_SET2/ | /59604F02/59607CD4/ | 596064D7
D |  |  |  |  |  |  |  |  |  |  |  |  |  | R7 | 7.5 | Resistors_SMD:R_0603_HandSoldering |  |  |  | device | R | /LED_Drive/IR_SET2/ | /59604F02/59607CD4/ | 59606544
D |  |  |  |  |  |  |  |  |  |  |  |  |  | D7 | CMDSH2-3 | Diodes_SMD:D_SOD-323_HandSoldering | http://www.mouser.com/ds/2/68/cmdsh2-3-39086.pdf | http://www.mouser.ch/ProductDetail/Central-Semiconductor/CMDSH2-3-TR/?qs=AjE1biBnhWMUdOF9vZ5x%252bg== | Buy Link | mynew_lib | CMDSH2-3 | /LED_Drive/IR_SET2/ | /59604F02/59607CD4/ | 597479DB
D |  |  |  |  |  |  |  |  |  |  |  |  |  | D7 | CMDSH2-3 | Diodes_SMD:D_SOD-323_HandSoldering | http://www.mouser.com/ds/2/68/cmdsh2-3-39086.pdf | CMDSH2-3 TR | MPN | mynew_lib | CMDSH2-3 | /LED_Drive/IR_SET2/ | /59604F02/59607CD4/ | 597479DB
D |  |  |  |  |  |  |  |  |  |  |  |  |  | U12 | MAX1561 | SparkFun-PowerIC:8-TDFN-EP | http://www.mouser.com/ds/2/256/MAX1561-MAX1599-65829.pdf | http://www.mouser.ch/ProductDetail/Maxim-Integrated/MAX1561ETA+T/?qs=p6VZ%252bklCkRSw1RT%2f%2fPr34Q== | Buy Link | MAX1599 | MAX1599 | /LED_Drive/IR_SET3/ | /59604F02/5960845F/ | 59604F14
D |  |  |  |  |  |  |  |  |  |  |  |  |  | U12 | MAX1561 | SparkFun-PowerIC:8-TDFN-EP | http://www.mouser.com/ds/2/256/MAX1561-MAX1599-65829.pdf | MAX1561ETA+T | MPN | MAX1599 | MAX1599 | /LED_Drive/IR_SET3/ | /59604F02/5960845F/ | 59604F14
D |  |  |  |  |  |  |  |  |  |  |  |  |  | C28 | 0.1uF | Capacitors_SMD:C_0603_HandSoldering |  |  |  | device | C | /LED_Drive/IR_SET3/ | /59604F02/5960845F/ | 5960555F
D |  |  |  |  |  |  |  |  |  |  |  |  |  | C27 | 2.2uF | Capacitors_SMD:C_0603_HandSoldering |  |  |  | device | C | /LED_Drive/IR_SET3/ | /59604F02/5960845F/ | 5960566F
D |  |  |  |  |  |  |  |  |  |  |  |  |  | C29 | 0.1uF | Capacitors_SMD:C_0603_HandSoldering |  |  |  | device | C | /LED_Drive/IR_SET3/ | /59604F02/5960845F/ | 5960587B
D |  |  |  |  |  |  |  |  |  |  |  |  |  | L4 | 47uH | Inductors_SMD:L_1210_HandSoldering |  |  |  | device | L | /LED_Drive/IR_SET3/ | /59604F02/5960845F/ | 59605DEA
D |  |  |  |  |  |  |  |  |  |  |  |  |  | D13 | LED | LEDs:LED_PLCC-2 |  |  |  | device | LED | /LED_Drive/IR_SET3/ | /59604F02/5960845F/ | 59606309
D |  |  |  |  |  |  |  |  |  |  |  |  |  | D14 | LED | LEDs:LED_PLCC-2 |  |  |  | device | LED | /LED_Drive/IR_SET3/ | /59604F02/5960845F/ | 596063DB
D |  |  |  |  |  |  |  |  |  |  |  |  |  | D15 | LED | LEDs:LED_PLCC-2 |  |  |  | device | LED | /LED_Drive/IR_SET3/ | /59604F02/5960845F/ | 596064A1
D |  |  |  |  |  |  |  |  |  |  |  |  |  | D16 | LED | LEDs:LED_PLCC-2 |  |  |  | device | LED | /LED_Drive/IR_SET3/ | /59604F02/5960845F/ | 596064D7
D |  |  |  |  |  |  |  |  |  |  |  |  |  | R8 | 7.5 | Resistors_SMD:R_0603_HandSoldering |  |  |  | device | R | /LED_Drive/IR_SET3/ | /59604F02/5960845F/ | 59606544
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

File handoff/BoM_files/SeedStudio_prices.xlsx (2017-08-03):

Component provider | Designator | MPN | SeeedSKU | Description | Quantity | Unit Price | Amount
Seeed | U2 | 105028-1001 | 508000001 | IC 及元件插座 8.5*8.5 AUTO FOCUS C AMERA SOCKET ASSY | 1 * 5 | 2.1026 | 10.513
Seeed | U1 | LM3670MFX-ADJ/NOPB | 508000001 | 轉換電壓穩壓器 Miniature Step-Down DC-DC Converter for Ultra Low Voltage Circuits 5-SOT-23 -40 to 85 | 1 * 5 | 1.0573 | 5.2865
Seeed | Y1 | ASFLMB-25.000MHZ-LC-T | 508000001 | 標準時鐘振盪器 25.000MHz 50ppm -40+85C | 1 * 5 | 1.5379 | 7.6895
Seeed | U4 | ADP150AUJZ-2.8-R7 | 508000001 | IC REG LDO 2.8V 0.15A TSOT23-5 | 1 * 5 | 1.3096 | 6.548
Seeed | U7,U5,U3 | ADP150AUJZ-3.3-R7 | 508000001 | 線性電壓穩壓器 Ultralow Noise 150mA CMOS | 3 * 5 | 1.0717 | 16.0755
Seeed | D1 | B340A-13-F | 508000001 | DIODE, RECTIFIER, 3A, 40V, DO-214AC | 1 * 5 | 0.4201 | 2.1005
Seeed | U6 | VL53L0CXV0DH/1 | 508000001 |  | 1 * 5 | 4.7164 | 23.582
Seeed | U8 | FIS1100 | 508000001 | IC, Special Function, Inertial Measurement Unit, 2.4 V-3 V supply, LGA-16 | 1 * 5 | 8.6158 | 43.079
Seeed | U9 | ADP150AUJZ-1.8-R7 | 508000001 | IC REG LDO 1.8V 0.15A TSOT23-5 | 1 * 5 | 1.3096 | 6.548
Seeed | D27,D22,D17,D12,D7,D2 | CMDSH2-3 TR | 508000001 | 肖特基二極體及整流器 30V Schottky | 6 * 5 | 0.5455 | 16.365
Seeed | U16 | BQ24075RGTR | 508000001 | 電池管理產品 Li-Ion Batt Chrgr & Pwr-Path Mgmt IC | 1 * 5 | 2.7033 | 13.5165
Seeed | J2 | 629105150521 | 508000001 | USB 連接器 WR-COM USB Micro SMT Type B Horiztl | 1 * 5 | 2.4871 | 12.4355
Seeed | Q2 | DMG2305UX-13 | 508000001 | MOSFET P-Ch ENH FET -20V 52mOhm -5.0V | 1 * 5 | 0.4566 | 2.283
Seeed | Q1 | DMMT5401-7-F | 508000001 | 雙極結晶體管 - BJT MATCHED PNP SM SIGNAL TRANS | 1 * 5 | 0.5166 | 2.583
 |  |  |  |  |  |  | 168.605

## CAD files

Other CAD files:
3d_model/sketchupfiles/CamPrj.skp
3d_model/sketchupfiles/CamPrj_alt_1.skp
3d_model/sketchupfiles/CamPrj_alt_2.skp
3d_model/sketchupfiles/PI_module.skp
3d_model/sketchupfiles/cam_module.skp
3d_model/sketchupfiles/pcb_module.skp

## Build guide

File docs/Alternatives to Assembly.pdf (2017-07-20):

# Alternatives to Assembly

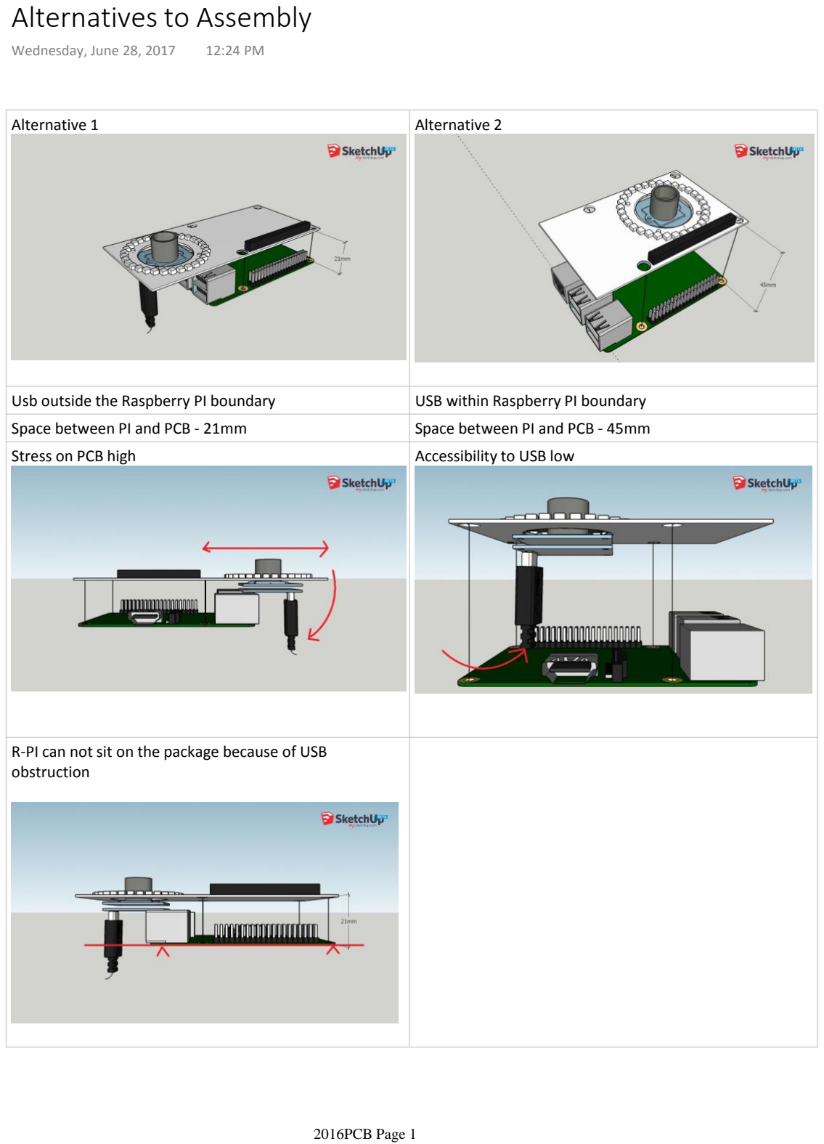
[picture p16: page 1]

Alternative 1 | Alternative 2
Usb outside the Raspberry PI boundary | USB within Raspberry PI boundary
Space between PI and PCB - 21mm | Space between PI and PCB - 45mm
Stress on PCB high | Accessibility to USB low

R-PI can not sit on the package because of USB obstruction

Wednesday, June 28, 2017 12:24 PM

2016PCB Page 1

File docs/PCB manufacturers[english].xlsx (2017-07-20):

Rigid PCB
 | A | B | C | D | e | F | G | H | I | J | K | L
1 | PCB manufacturers
2
3 | Stand: 12.8.15, Michael Herold-Nadig
4
5 | PCB-Pool | https://www.pcb-pool.com/ppde/index.html (https://translate.google.com/translate?hl=en&prev=_t&sl=auto&tl=en&u=https://www.pcb-pool.com/ppde/index.html) | Free combination of seperation, sep. Cut-out of individual prints = 12 €.Various prints made by SMS da. Solder resist does not work well (eg fonts in the solder stop). File to upload = * .PCBDOC |  |  |  | Bastli files, which need to be uploaded (status 2.2013), see also project: P: \ Electronic Workshop \ SMS PCBs \ PCB data of individual projects \ SMS-1.2013 Prosthesis PT100 Amplifier \ eagle \ GERBER for BASTLI
6 | Bastli ETHZ | http://people.ee.ethz.ch/~bastli/index.php? (https://translate.google.com/translate?hl=en&prev=_t&sl=auto&tl=en&u=http://people.ee.ethz.ch/~bastli/index.php%3F) | LPFK-milling machine without through-holes & soldering stop. For simple designs, rel. inexpensive. Accept only Gerber (-X) files. Due to the packages, it is worth taking a look (see https://pcb.bastli.ch/pricing).
7 | PCB Card | www.pcbcart.com (https://translate.google.com/translate?hl=en&prev=_t&sl=auto&tl=en&u=http://www.pcbcart.com/) | Chinese producer, very cheap. RELAB makes his prints there. There is also a placement service and altium data are accepted directly.
8th | multi.cb | http://www.multi-circuit-boards.eu (https://translate.google.com/translate?hl=en&prev=_t&sl=auto&tl=en&u=http://www.multi-circuit-boards.eu/) | Various prints made by SMS da. Very cheap with express service (2 AT, 2 layers, Cybathlon). Large selection of surfaces and laminates. Currently (6.2012) no Altium data but ODB ++ can be accepted.
9 | Würth Electronics | www.wedirekt.de (https://translate.google.com/translate?hl=en&prev=_t&sl=auto&tl=en&u=http://www.wedirekt.de/) | Very cheap, if no paste template is necessary. And even with thinner circuit boards (1 mm) much cheaper than the others.
10 | euro circuits | http://www.eurocircuits.com/ (https://translate.google.com/translate?hl=en&prev=_t&sl=auto&tl=en&u=http://www.eurocircuits.com/) | Hocoma has already produced prints there.
11 | TOM-IC.com | http://www.tom-ic.com/tic/index.php/de/bestellung (https://translate.google.com/translate?hl=en&prev=_t&sl=auto&tl=en) | Kamen introduce themselves in ETH (ASL-Lab), well there in CH (advertisement via e-mail from 25.11.13 to hermicha)
12
13 | Ke Jie PCB Manufacturing | www.kejiepcb.com (https://translate.google.com/translate?hl=en&prev=_t&sl=auto&tl=en&u=http://www.kejiepcb.com/) | China. Very cheap Cybathlon-Cigarette-Flex-Print (half price against second-billing). Fast delivery time.
14 | flexible Circuit | www.flexiblecircuit.com (https://translate.google.com/translate?hl=en&prev=_t&sl=auto&tl=en&u=http://www.flexiblecircuit.com/) | Request made
15 | FlexPCB | www.flexpcb.com/quote (https://translate.google.com/translate?hl=en&prev=_t&sl=auto&tl=en&u=http://www.flexpcb.com/quote) | Request made
16 | Leiton | www.leiton.de (https://translate.google.com/translate?hl=en&prev=_t&sl=auto&tl=en&u=http://www.leiton.de/) | Favorable flex circuit boards. Plants in Germany and China.
17 | Pentalogix | www.pentalogix.com (https://translate.google.com/translate?hl=en&prev=_t&sl=auto&tl=en&u=http://www.pentalogix.com/) | US Printersteller with offshoot in China for Low Price.
18 | ALWA Print | http://www.alwaprint.ch (https://translate.google.com/translate?hl=en&prev=_t&sl=auto&tl=en&u=http://www.alwaprint.ch/) | CH manufacturer with various substrates (also rigid / flex print). For small series.
19 | Platinenbelichter | http://platinenbelichter.de (https://translate.google.com/translate?hl=en&prev=_t&sl=auto&tl=en&u=http://platinenbelichter.de/) | Very cheap service (quality modest), was used by Christoph Hollnagel times privately. It takes a long time (at least 14 days).
20 | VarioPrint | http://www.varioprint.ch (https://translate.google.com/translate?hl=en&prev=_t&sl=auto&tl=en&u=http://www.varioprint.ch/) | CH manufacturers of high-quality printed circuit boards.
21 | Optiprint | http://www.optiprint.ch (https://translate.google.com/translate?hl=en&prev=_t&sl=auto&tl=en&u=http://www.optiprint.ch/) | CH manufacturers of high-quality printed circuit boards.
22 | Swiss | http://www.schweizer.ag (https://translate.google.com/translate?hl=en&prev=_t&sl=auto&tl=en&u=http://www.schweizer.ag/) | DE manufacturers of high-quality printed circuit boards.
23
24 | TEC Microsystems | http://www.tec-microsystems.com/EN/Ceramics_Substrates.html (https://translate.google.com/translate?hl=en&prev=_t&sl=auto&tl=en) | Ceramic base material (good heat dissipation), possibly alternative to the aluminum core of eg PCB pool.
25
26
27 | If Altium format is not accepted directly, ODB ++ can be exported (more modern than Gerber) instead.
Flex PCB
 | A | B | C | D | e | F | G
1 | Compilation of the offerings for Flex-PCBs for Cybathlon light driers
2 | Stand: 19.4.16, Michael Herold-Nadig
3 |  |  |  |  | Request for flex PCB 140 x 94 mm2 with any 3M adhesive film on the back, 2 LAY
4 | PCB-Pool | www.pcb-pool.com/ppde/index.html (https://translate.google.com/translate?hl=en&prev=_t&sl=auto&tl=en&u=http://www.pcb-pool.com/ppde/index.html) | Free combination of seperation, sep. Cut-out of individual prints = 12 €.Various prints made by SMS da. |  | 4312 € | 22 AT
5 | PCB Card | www.pcbcart.com (https://translate.google.com/translate?hl=en&prev=_t&sl=auto&tl=en&u=http://www.pcbcart.com/) | Chinese producer, very cheap. RELAB makes his prints there. There is also a placement service and altium data are accepted directly. |  | 460.10 $ + shipping, no adhesive film possible | 10 AT
6 | multi.cb | http://www.multi-circuit-boards.eu (https://translate.google.com/translate?hl=en&prev=_t&sl=auto&tl=en&u=http://www.multi-circuit-boards.eu/) | Various prints made by SMS da. Very cheap with express service (2 AT, 2 layers, Cybathlon). Large selection of surfaces and laminates. |  | 668 € resp. 822 € with adhesive film | 15 AT
7 | Würth Electronics | www.wedirekt.de (https://translate.google.com/translate?hl=en&prev=_t&sl=auto&tl=en&u=http://www.wedirekt.de/) | Very cheap, if no paste template is necessary. And even with thinner circuit boards (1 mm) much cheaper than the others. |  | 1929 € | 10 AT
8th | Ke Jie PCB Manufacturing | www.kejiepcb.com (https://translate.google.com/translate?hl=en&prev=_t&sl=auto&tl=en&u=http://www.kejiepcb.com/) | China. Very cheap Cybathlon-Cigarette-Flex-Print (half price against second-billing). Fast delivery time. |  | 429 $ incl. Adhesive film | 7 AT (+6 d for shipping) | This manufacturer selected for Cybathlon Cube-LED-Print, 15.4.16, MH.
9 | flexible Circuit | www.flexiblecircuit.com (https://translate.google.com/translate?hl=en&prev=_t&sl=auto&tl=en&u=http://www.flexiblecircuit.com/) | Found in the Internet. |  | 1550 $ | 20 AT
10 | FlexPCB | www.flexpcb.com/quote (https://translate.google.com/translate?hl=en&prev=_t&sl=auto&tl=en&u=http://www.flexpcb.com/quote) | Found in the Internet. |  | $ 1493 to $ 2146 plus $ 200 each tooling costs. | 8 AT to 5 AT
11 | Leiton | www.leiton.de (https://translate.google.com/translate?hl=en&prev=_t&sl=auto&tl=en&u=http://www.leiton.de/) | Relatively cheap. Plants in Germany and China. |  | 1114 €, adhesive film possible | 12 AT

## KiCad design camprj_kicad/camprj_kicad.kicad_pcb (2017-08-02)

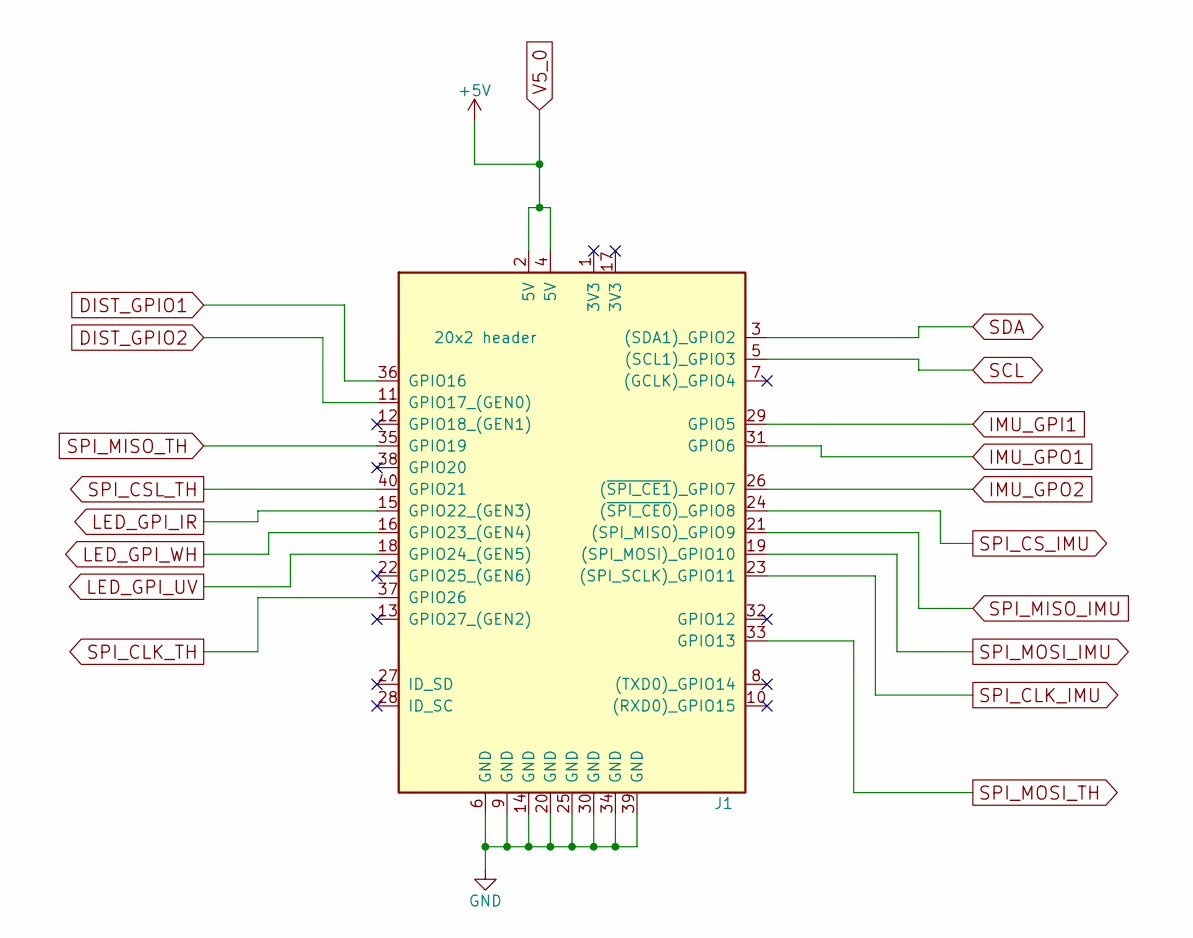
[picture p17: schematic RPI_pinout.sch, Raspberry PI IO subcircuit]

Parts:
J1: 20x2 header; Pin_Header_Straight_2x20_Pitch2.54mm; MPN ESQ-120-69-G-D-LL

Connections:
DIST_GPIO1: J1.36 (GPIO16); also elsewhere on the board
DIST_GPIO2: J1.11 (GPIO17_(GEN0)); also elsewhere on the board
GND: J1.6 (GND), J1.9 (GND), J1.14 (GND), J1.20 (GND), J1.25 (GND), J1.30 (GND), J1.34 (GND), J1.39 (GND); also elsewhere on the board
IMU_GPI1: J1.29 (GPIO5); also elsewhere on the board
IMU_GPO1: J1.31 (GPIO6); also elsewhere on the board
IMU_GPO2: J1.26 ((~SPI_CE1~)_GPIO7); also elsewhere on the board
LED_GPI_IR: J1.15 (GPIO22_(GEN3)); also elsewhere on the board
LED_GPI_UV: J1.18 (GPIO24_(GEN5)); also elsewhere on the board
LED_GPI_WH: J1.16 (GPIO23_(GEN4)); also elsewhere on the board
SCL: J1.5 ((SCL1)_GPIO3); also elsewhere on the board
SDA: J1.3 ((SDA1)_GPIO2); also elsewhere on the board
SPI_CLK_IMU: J1.23 ((SPI_SCLK)_GPIO11); also elsewhere on the board
SPI_CLK_TH: J1.37 (GPIO26); also elsewhere on the board
SPI_CSL_TH: J1.40 (GPIO21); also elsewhere on the board
SPI_CS_IMU: J1.24 ((~SPI_CE0~)_GPIO8); also elsewhere on the board
SPI_MISO_IMU: J1.21 ((SPI_MISO)_GPIO9); also elsewhere on the board
SPI_MISO_TH: J1.35 (GPIO19); also elsewhere on the board
SPI_MOSI_IMU: J1.19 ((SPI_MOSI)_GPIO10); also elsewhere on the board
SPI_MOSI_TH: J1.33 (GPIO13); also elsewhere on the board
V5_0: J1.2 (5V), J1.4 (5V); also elsewhere on the board

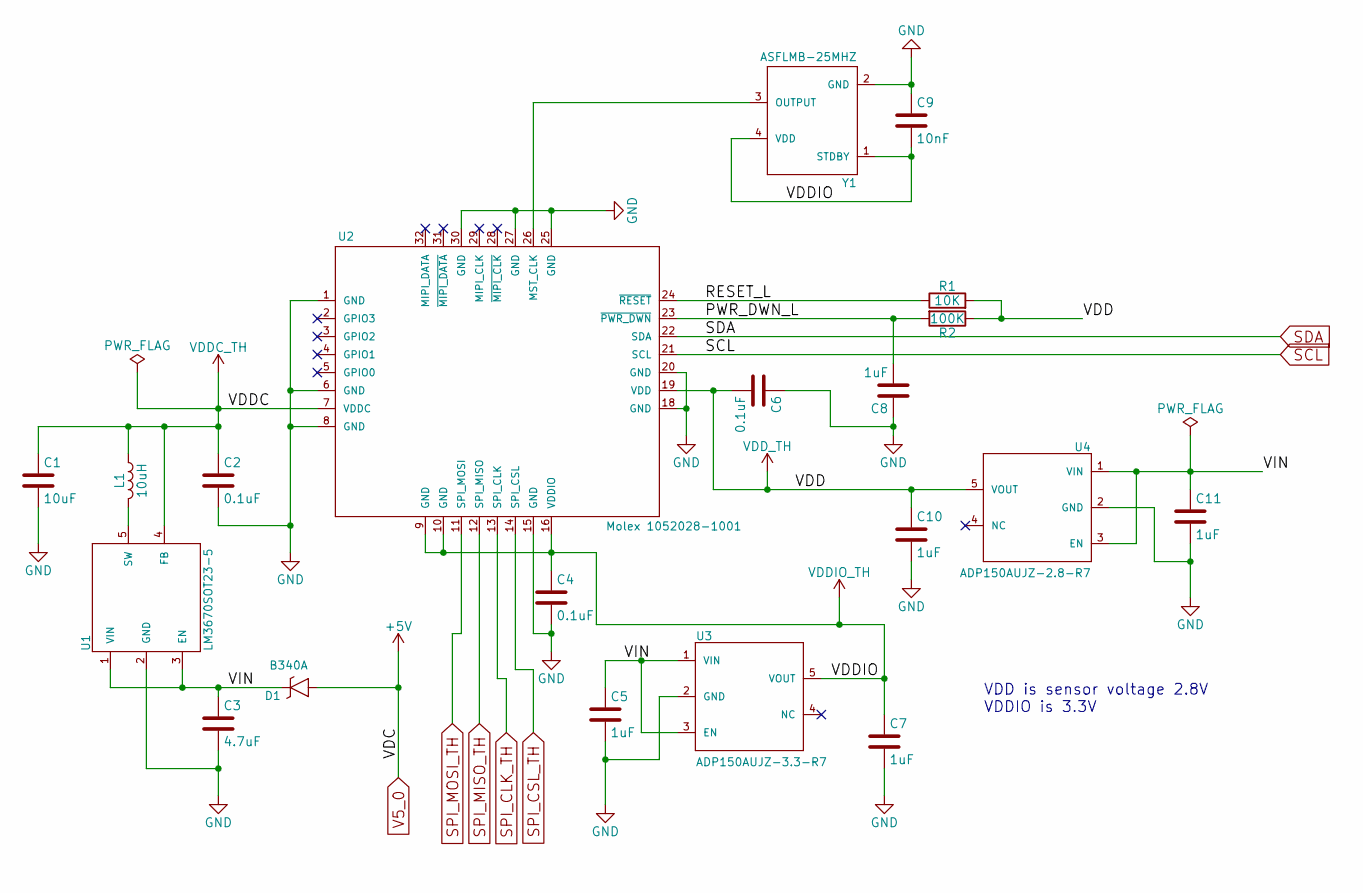
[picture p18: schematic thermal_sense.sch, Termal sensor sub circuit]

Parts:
C1: 10uF; C_0603_HandSoldering
C2, C4, C6: 0.1uF; C_0603_HandSoldering
C3: 4.7uF; C_0603_HandSoldering
C5, C7, C8, C10, C11: 1uF; C_0603_HandSoldering
C9: 10nF; C_0603_HandSoldering
D1: B340A; D_SMA_Handsoldering_AC; MPN B340A-13-F
L1: 10uH; L_1210_HandSoldering
R1: 10K; R_0603_HandSoldering
R2: 100K; R_0603_HandSoldering
U1: LM3670SOT23-5; SOT-23-5_HandSoldering; MPN LM3670MFX-ADJ/NOPB
U2: Molex 1052028-1001; 105028-1001; MPN 105028-1001
U3: ADP150AUJZ-3.3-R7; TSOT-23-5_HandSoldering; MPN ADP150AUJZ-3.3-R7
U4: ADP150AUJZ-2.8-R7; TSOT-23-5_HandSoldering; MPN ADP150AUJZ-2.8-R7
Y1: ASFLMB-25MHZ; 5X3.2-CRYSTAL; MPN ASFLMB-25.000MHZ-LC-T

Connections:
/thermal_sense/PWR_DWN_L: C8.2, R2.2, U2.23 (~PWR_DWN)
/thermal_sense/RESET_L: R1.1, U2.24 (~RESET)
/thermal_sense/VIN: C3.1, C5.1, C11.1, D1.C, U1.1 (VIN), U1.3 (EN), U3.1 (VIN), U3.3 (EN), U4.1 (VIN), U4.3 (EN)
GND: C1.2, C2.2, C3.2, C4.2, C5.2, C6.1, C7.2, C8.1, C9.1, C10.2, C11.2, U1.2 (GND), U2.1 (GND), U2.6 (GND), U2.8 (GND), U2.15 (GND), U2.18 (GND), U2.20 (GND), U2.25 (GND), U2.27 (GND), U2.30 (GND), U3.2 (GND), U4.2 (GND), Y1.2 (GND); also elsewhere on the board
unnamed: L1.2, U1.5 (SW)
unnamed: U2.26 (MST_CLK), Y1.3 (OUTPUT)
SCL: U2.21 (SCL); also elsewhere on the board
SDA: U2.22 (SDA); also elsewhere on the board
SPI_CLK_TH: U2.13 (SPI_CLK); also elsewhere on the board
SPI_CSL_TH: U2.14 (SPI_CSL); also elsewhere on the board
SPI_MISO_TH: U2.12 (SPI_MISO); also elsewhere on the board
SPI_MOSI_TH: U2.11 (SPI_MOSI); also elsewhere on the board
V5_0: D1.A; also elsewhere on the board
VDDC_TH: C1.1, C2.1, L1.1, U1.4 (FB), U2.7 (VDDC)
VDDIO_TH: C4.1, C7.1, C9.2, U2.9 (GND), U2.10 (GND), U2.16 (VDDIO), U3.5 (VOUT), Y1.1 (STDBY), Y1.4 (VDD)
VDD_TH: C6.2, C10.1, R1.2, R2.1, U2.19 (VDD), U4.5 (VOUT)

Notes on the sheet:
VDD is sensor voltage 2.8V VDDIO is 3.3V

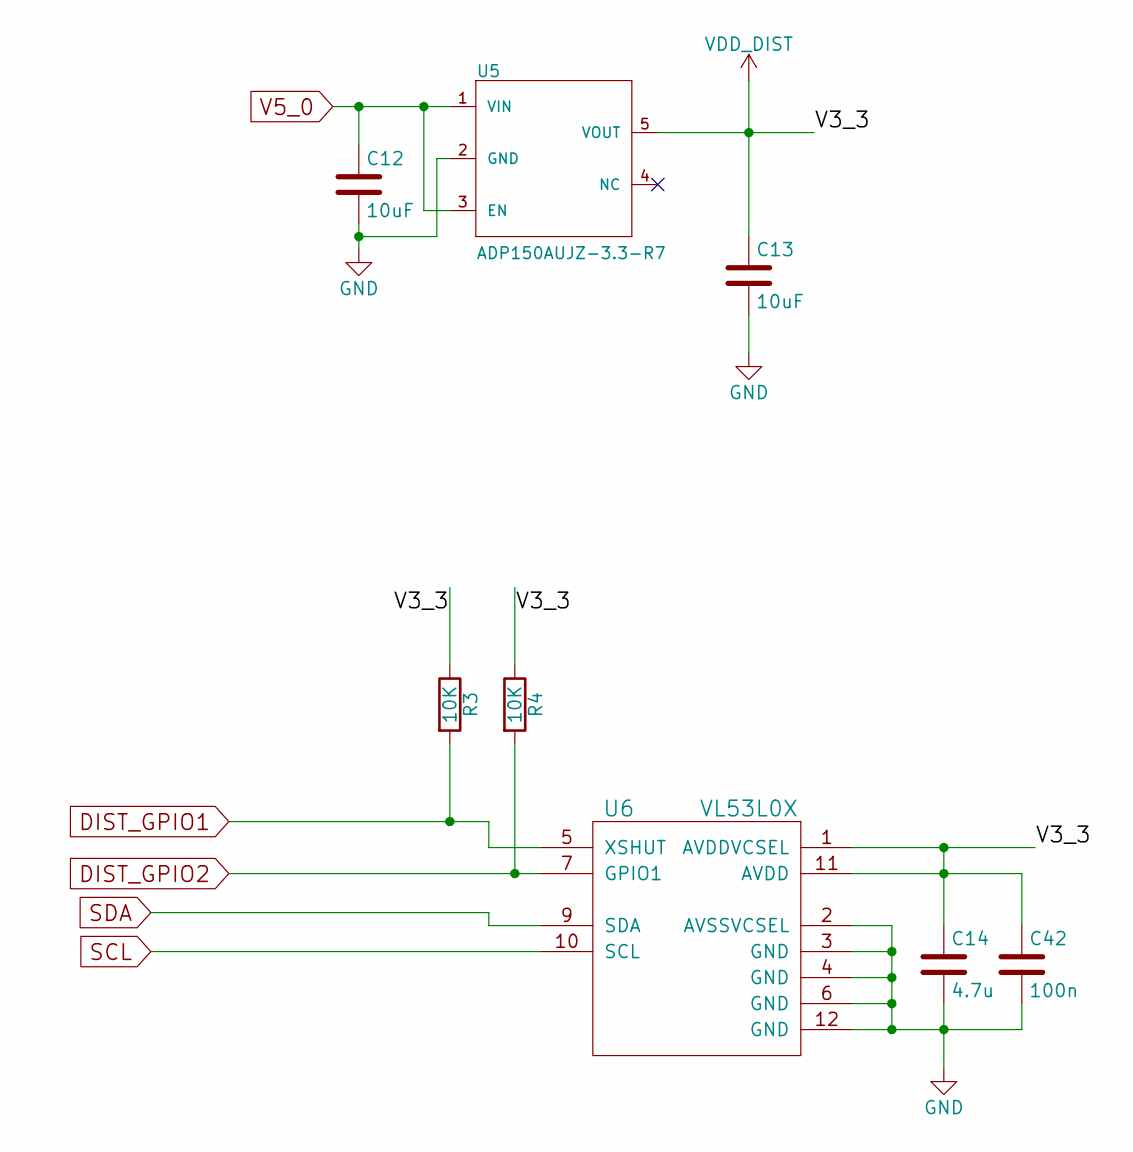
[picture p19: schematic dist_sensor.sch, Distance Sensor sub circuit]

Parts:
C12, C13: 10uF; C_0603_HandSoldering
C14: 4.7u; C_0603_HandSoldering
C42: 100n; C_0603_HandSoldering
R3, R4: 10K; R_0603_HandSoldering
U5: ADP150AUJZ-3.3-R7; TSOT-23-5_HandSoldering; MPN ADP150AUJZ-3.3-R7
U6: VL53L0X; Optical_LGA12; MPN VL53L0CXV0DH/1

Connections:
DIST_GPIO1: R3.2, U6.5 (XSHUT); also elsewhere on the board
DIST_GPIO2: R4.2, U6.7 (GPIO1); also elsewhere on the board
GND: C12.2, C13.2, C14.2, C42.2, U5.2 (GND), U6.2 (AVSSVCSEL), U6.3 (GND), U6.4 (GND), U6.6 (GND), U6.12 (GND); also elsewhere on the board
SCL: U6.10 (SCL); also elsewhere on the board
SDA: U6.9 (SDA); also elsewhere on the board
V5_0: C12.1, U5.1 (VIN), U5.3 (EN); also elsewhere on the board
VDD_DIST: C13.1, C14.1, C42.1, R3.1, R4.1, U5.5 (VOUT), U6.1 (AVDDVCSEL), U6.11 (AVDD)

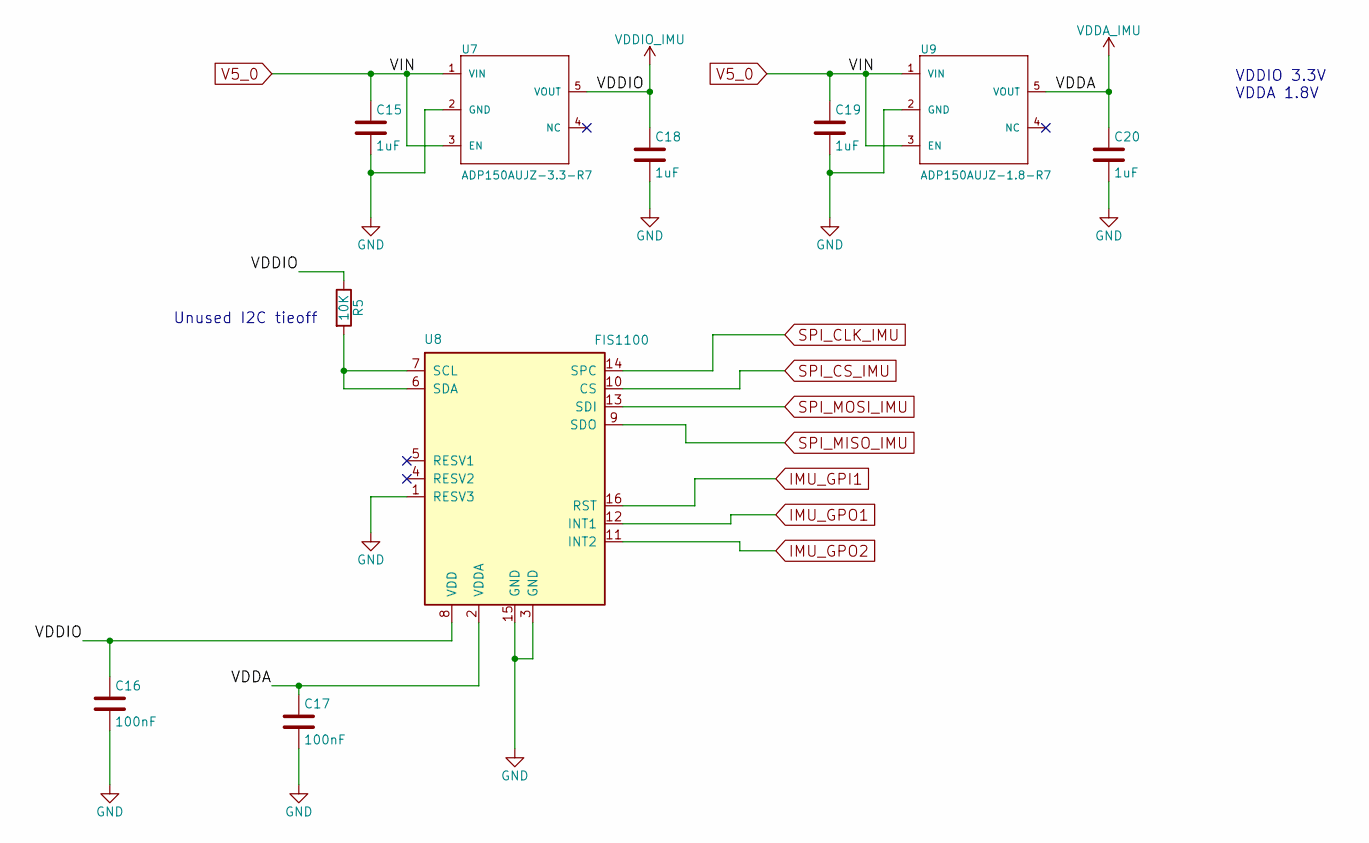
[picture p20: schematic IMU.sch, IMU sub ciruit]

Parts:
C15, C18, C19, C20: 1uF; C_0603_HandSoldering
C16, C17: 100nF; C_0603_HandSoldering
R5: 10K; R_0603_HandSoldering
U7: ADP150AUJZ-3.3-R7; TSOT-23-5_HandSoldering; MPN ADP150AUJZ-3.3-R7
U8: FIS1100; LGA16; MPN FIS1100
U9: ADP150AUJZ-1.8-R7; TSOT-23-5_HandSoldering; MPN ADP150AUJZ-1.8-R7

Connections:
GND: C15.2, C16.2, C17.2, C18.2, C19.2, C20.2, U7.2 (GND), U8.1 (RESV3), U8.3 (GND), U8.15 (GND), U9.2 (GND); also elsewhere on the board
IMU_GPI1: U8.16 (RST); also elsewhere on the board
IMU_GPO1: U8.12 (INT1); also elsewhere on the board
IMU_GPO2: U8.11 (INT2); also elsewhere on the board
unnamed: R5.2, U8.6 (SDA), U8.7 (SCL)
SPI_CLK_IMU: U8.14 (SPC); also elsewhere on the board
SPI_CS_IMU: U8.10 (CS); also elsewhere on the board
SPI_MISO_IMU: U8.9 (SDO); also elsewhere on the board
SPI_MOSI_IMU: U8.13 (SDI); also elsewhere on the board
V5_0: C15.1, C19.1, U7.1 (VIN), U7.3 (EN), U9.1 (VIN), U9.3 (EN); also elsewhere on the board
VDDA_IMU: C17.1, C20.1, U8.2 (VDDA), U9.5 (VOUT)
VDDIO_IMU: C16.1, C18.1, R5.1, U7.5 (VOUT), U8.8 (VDD)

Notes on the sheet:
VDDIO 3.3V VDDA 1.8V
Unused I2C tieoff

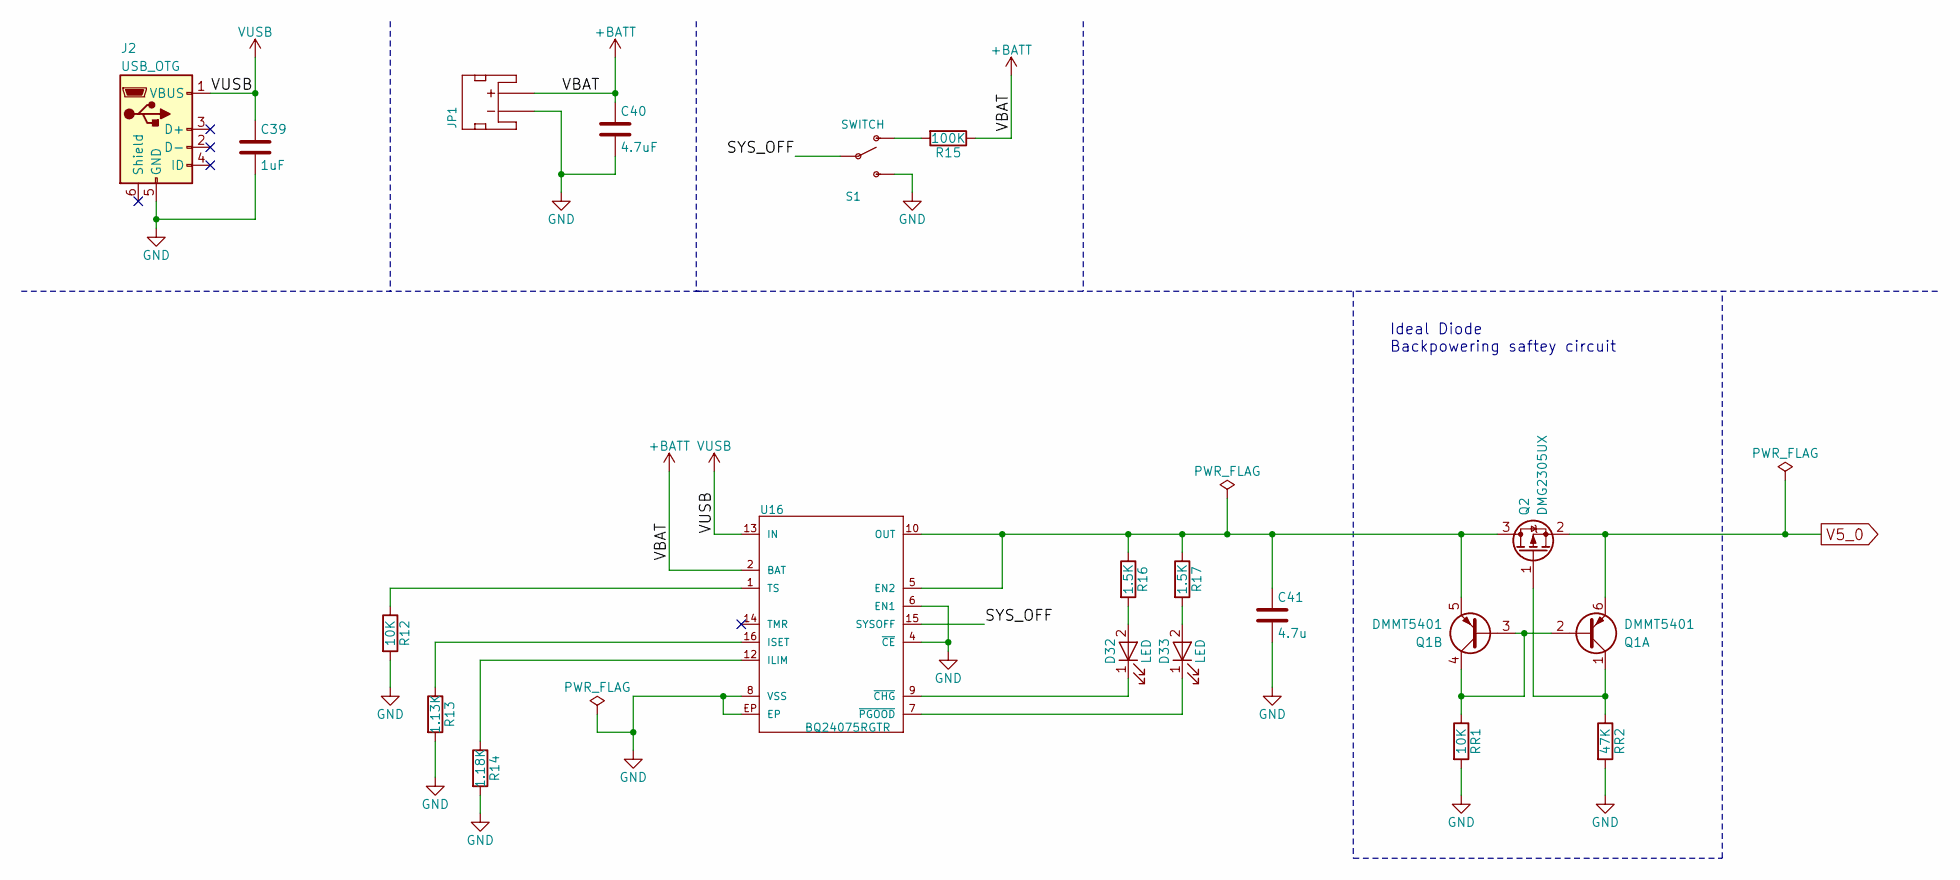
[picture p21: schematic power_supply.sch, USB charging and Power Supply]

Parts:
C39: 1uF; C_0603_HandSoldering
C40: 4.7uF; C_0603_HandSoldering
C41: 4.7u; C_0603_HandSoldering
D32, D33: LED; LED_PLCC-2
J2: USB_OTG; USB_Micro-B; MPN 629105150521
JP1: JST_2MM_MALE; JST_PH_B2B-PH-K_02x2.00mm_Straight; MPN BM02B-CPTK-1A-TB
Q1: DMMT5401; SOT-23-6_Handsoldering; MPN DMMT5401-7-F
Q2: DMG2305UX; SOT-23; MPN DMG2305UX-13
R12: 10K; R_0603_HandSoldering
R13: 1.13K; R_0603_HandSoldering
R14: 1.18K; R_0603_HandSoldering
R15: 100K; R_0603_HandSoldering
R16, R17: 1.5K; R_0603_HandSoldering
RR1: 10K; R_0603_HandSoldering
RR2: 47K; R_0603_HandSoldering
S1: SWITCH; DPST_TE_SSJ12R04; MPN 1825282-1
U16: BQ24075RGTR; QFN-16-1EP_3x3mm_Pitch0.5mm; MPN BQ24075RGTR

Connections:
+BATT: C40.1, JP1.2 (+), R15.1, U16.2 (BAT), U16.3 (BAT)
/power_supply/SYS_OFF: S1.2, U16.15 (SYSOFF)
GND: C39.2, C40.2, C41.2, J2.5 (GND), JP1.1 (-), R12.2, R13.2, R14.2, RR1.2, RR2.2, S1.3 (S), U16.4 (~CE~), U16.6 (EN1), U16.8 (VSS), U16.EP; also elsewhere on the board
unnamed: C41.1, Q1.5 (E2), Q2.3 (D), R16.1, R17.1, U16.5 (EN2), U16.10 (OUT), U16.11 (OUT)
unnamed: D32.1 (K), U16.9 (~CHG~)
unnamed: D32.2 (A), R16.2
unnamed: D33.1 (K), U16.7 (~PGOOD~)
unnamed: D33.2 (A), R17.2
unnamed: Q1.1 (C1), Q2.1 (G), RR2.1
unnamed: Q1.2 (B1), Q1.3 (B2), Q1.4 (C2), RR1.1
unnamed: R12.1, U16.1 (TS)
unnamed: R13.1, U16.16 (ISET)
unnamed: R14.1, U16.12 (ILIM)
unnamed: R15.2, S1.1 (O)
V5_0: Q1.6 (E1), Q2.2 (S); also elsewhere on the board
VUSB: C39.1, J2.1 (VBUS), U16.13 (IN)

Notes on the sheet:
Ideal Diode Backpowering saftey circuit

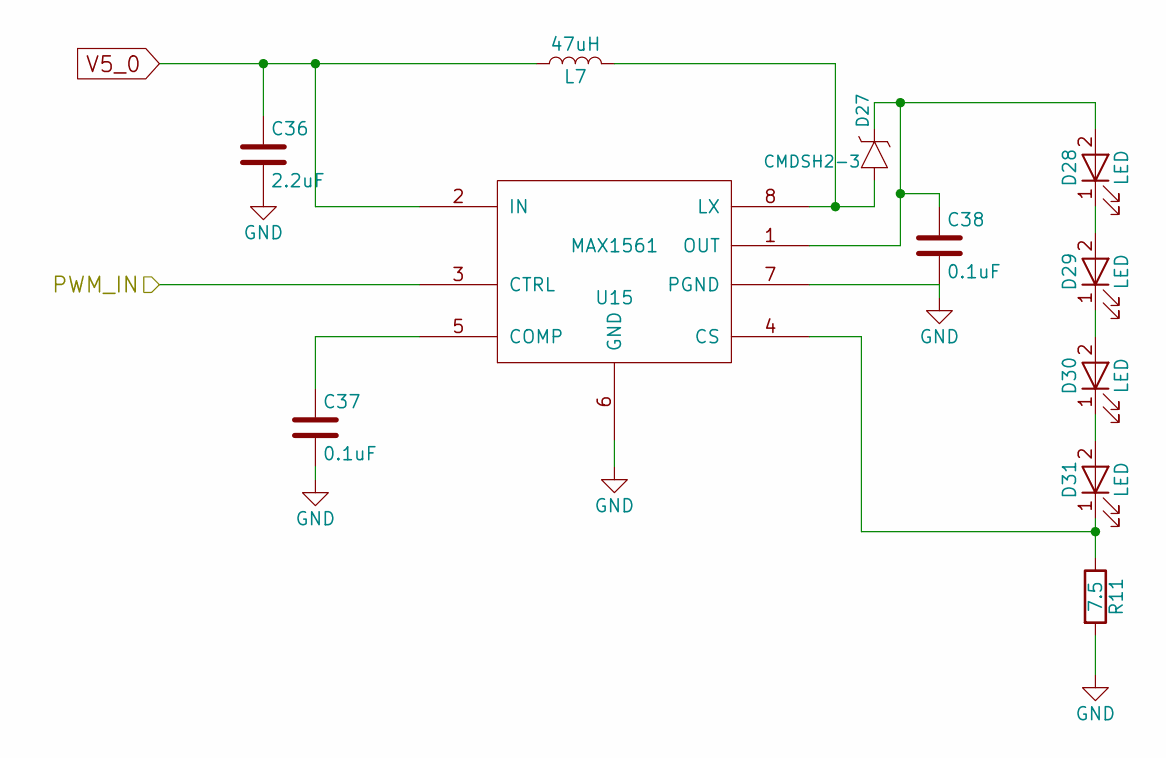
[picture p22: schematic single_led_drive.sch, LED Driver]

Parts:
C24: 2.2uF; C_0603_HandSoldering
C25, C26: 0.1uF; C_0603_HandSoldering
D8, D9, D10, D11: LED; LED_PLCC-2
D12: CMDSH2-3; D_SOD-323_HandSoldering; MPN CMDSH2-3 TR
L3: 47uH; L_1210_HandSoldering
R7: 7.5; R_0603_HandSoldering
U11: MAX1561; 8-TDFN-EP; MPN MAX1561ETA+T

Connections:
GND: C24.2, C25.2, C26.2, R7.2, U11.6 (GND), U11.7 (PGND), U11.9 (EP); also elsewhere on the board
LED_GPI_IR: U11.3 (CTRL); also elsewhere on the board
unnamed: C25.1, U11.5 (COMP)
unnamed: D8.1 (K), D9.2 (A)
unnamed: D10.1 (K), D11.2 (A)
unnamed: D9.1 (K), D10.2 (A)
unnamed: D11.1 (K), R7.1, U11.4 (CS)
V5_0: C24.1, L3.1, U11.2 (IN); also elsewhere on the board

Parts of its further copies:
C21, C27, C30, C33, C36: 2.2uF; C_0603_HandSoldering
C22, C23, C28, C29, C31, C32, C34, C35, C37, C38: 0.1uF; C_0603_HandSoldering
D2, D7, D17, D22, D27: CMDSH2-3; D_SOD-323_HandSoldering; MPN CMDSH2-3 TR
D3, D4, D5, D6, D13, D14, D15, D16, D18, D19, D20, D21, D23, D24, D25, D26, D28, D29, D30, D31: LED; LED_PLCC-2
L2, L4, L5, L6, L7: 47uH; L_1210_HandSoldering
R6, R8, R9, R10, R11: 7.5; R_0603_HandSoldering
U10, U12, U13, U14, U15: MAX1561; 8-TDFN-EP; MPN MAX1561ETA+T

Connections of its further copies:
/LED_Drive/IR_SET3/PWM_IN: U12.3 (CTRL)
GND: C21.2, C22.2, C23.2, C27.2, C28.2, C29.2, C30.2, C31.2, C32.2, C33.2, C34.2, C35.2, C36.2, C37.2, C38.2, R6.2, R8.2, R9.2, R10.2, R11.2, U10.6 (GND), U10.7 (PGND), U10.9 (EP), U12.6 (GND), U12.7 (PGND), U12.9 (EP), U13.6 (GND), U13.7 (PGND), U13.9 (EP), U14.6 (GND), U14.7 (PGND), U14.9 (EP), U15.6 (GND), U15.7 (PGND), U15.9 (EP); also elsewhere on the board
LED_GPI_IR: U10.3 (CTRL), U13.3 (CTRL); also elsewhere on the board
LED_GPI_UV: U15.3 (CTRL); also elsewhere on the board
LED_GPI_WH: U14.3 (CTRL); also elsewhere on the board
unnamed: C22.1, U10.5 (COMP)
unnamed: C23.1, D2.2, D3.2 (A), U10.1 (OUT)
unnamed: C28.1, U12.5 (COMP)
unnamed: C31.1, U13.5 (COMP)
unnamed: C32.1, D17.2, D18.2 (A), U13.1 (OUT)
unnamed: C34.1, U14.5 (COMP)
unnamed: C35.1, D22.2, D23.2 (A), U14.1 (OUT)
unnamed: C37.1, U15.5 (COMP)
unnamed: C38.1, D27.2, D28.2 (A), U15.1 (OUT)
unnamed: D2.1, L2.2, U10.8 (LX)
unnamed: D3.1 (K), D4.2 (A)
unnamed: D4.1 (K), D5.2 (A)
unnamed: D5.1 (K), D6.2 (A)
unnamed: D6.1 (K), R6.1, U10.4 (CS)
unnamed: D13.1 (K), D14.2 (A)
unnamed: D14.1 (K), D15.2 (A)
unnamed: D15.1 (K), D16.2 (A)
unnamed: D16.1 (K), R8.1, U12.4 (CS)
unnamed: D17.1, L5.2, U13.8 (LX)
unnamed: D18.1 (K), D19.2 (A)
unnamed: D19.1 (K), D20.2 (A)
unnamed: D20.1 (K), D21.2 (A)
unnamed: D21.1 (K), R9.1, U13.4 (CS)
unnamed: D22.1, L6.2, U14.8 (LX)
unnamed: D23.1 (K), D24.2 (A)
unnamed: D24.1 (K), D25.2 (A)
unnamed: D25.1 (K), D26.2 (A)
unnamed: D26.1 (K), R10.1, U14.4 (CS)
unnamed: D27.1, L7.2, U15.8 (LX)
unnamed: D28.1 (K), D29.2 (A)
unnamed: D29.1 (K), D30.2 (A)
unnamed: D30.1 (K), D31.2 (A)
unnamed: D31.1 (K), R11.1, U15.4 (CS)
V5_0: C21.1, C27.1, C30.1, C33.1, C36.1, L2.1, L4.1, L5.1, L6.1, L7.1, U10.2 (IN), U12.2 (IN), U13.2 (IN), U14.2 (IN), U15.2 (IN); also elsewhere on the board

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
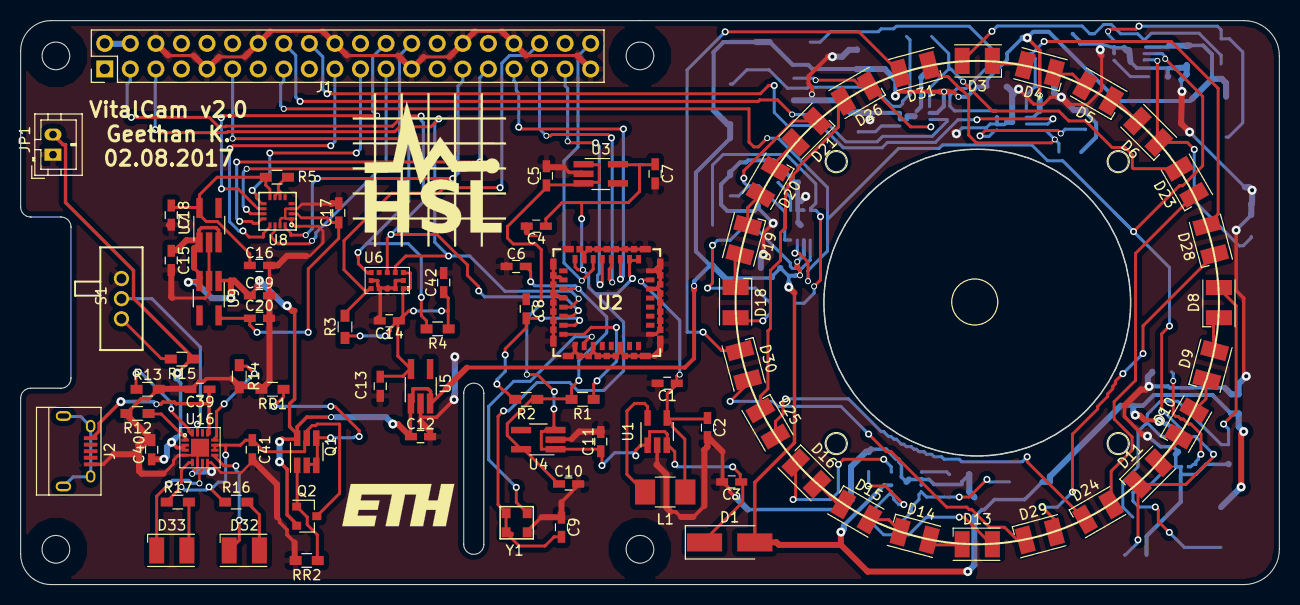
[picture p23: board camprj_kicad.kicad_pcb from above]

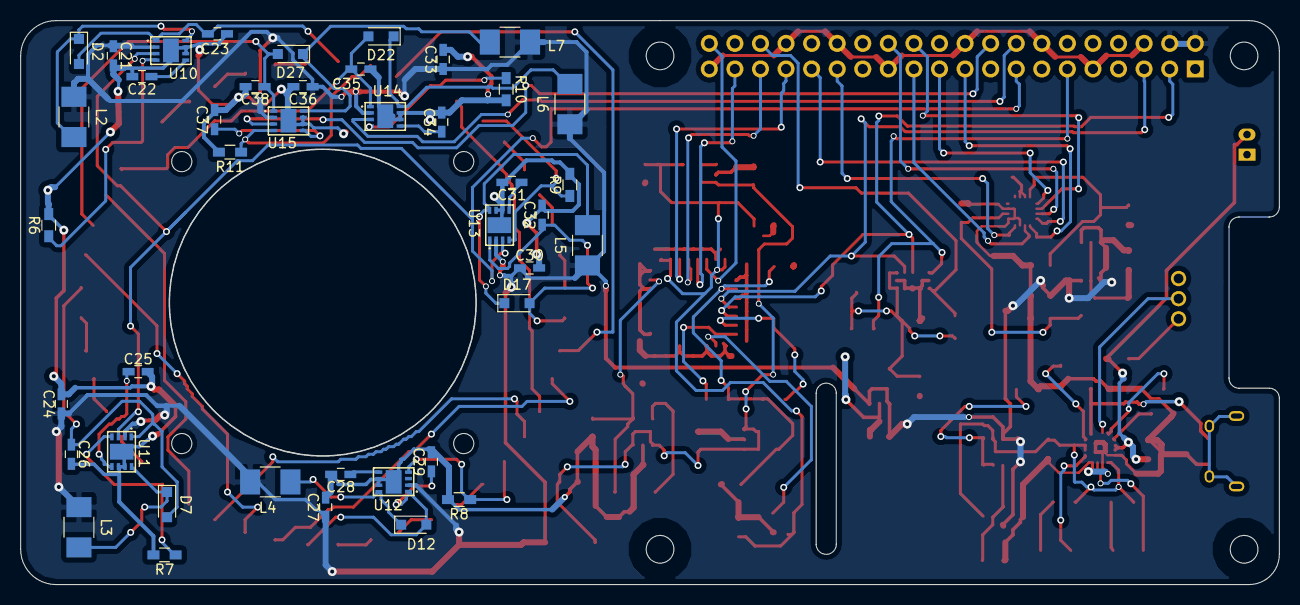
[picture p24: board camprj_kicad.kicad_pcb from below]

Board: 2 copper layers, 125.0 x 56.0 mm, 124 parts (42 on the bottom side), 88 nets.

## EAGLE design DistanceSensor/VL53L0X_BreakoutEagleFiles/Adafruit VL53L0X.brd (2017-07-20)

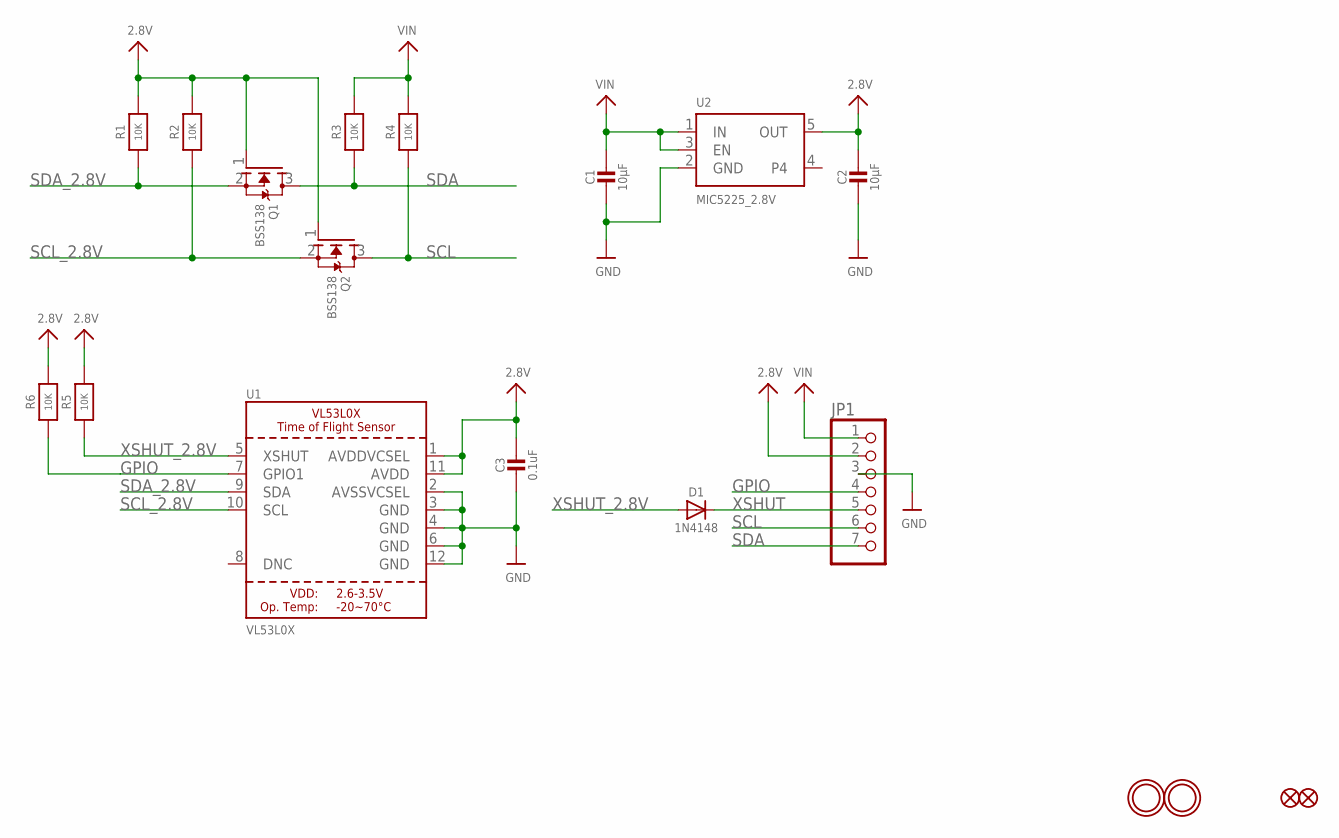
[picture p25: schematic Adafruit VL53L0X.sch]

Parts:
C1, C2: 10µF; 0805-NO
C3: 0.1uF; 0805-NO
D1: 1N4148; SOD-323
FID2, FID3: FIDUCIAL""; FIDUCIAL_1MM
JP1: HEADER-1X770MIL; 1X07_ROUND_70
Q1, Q2: BSS138; SOT23-WIDE
R1, R2, R3, R4, R5, R6: 10K; 0805-NO
U1: VL53L0X; LGA12_ST
U2: MIC5225_2.8V; SOT23-5
U$13, U$14: MOUNTINGHOLE2.5; MOUNTINGHOLE_2.5_PLATED

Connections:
2.8V: C2.1, C3.1, JP1.2, Q1.1 (G), Q2.1 (G), R1.2, R2.2, R5.2, R6.2, U1.1 (AVDDVCSEL), U1.11 (AVDD), U2.5 (OUT)
GND: C1.2, C2.2, C3.2, JP1.3, U1.2 (AVSSVCSEL), U1.3 (GND), U1.4 (GND), U1.6 (GND), U1.12 (GND), U2.2 (GND)
GPIO: JP1.4, R6.1, U1.7 (GPIO1)
SCL: JP1.6, Q2.3 (D), R4.1
SCL_2.8V: Q2.2 (S), R2.1, U1.10 (SCL)
SDA: JP1.7, Q1.3 (D), R3.1
SDA_2.8V: Q1.2 (S), R1.1, U1.9 (SDA)
VIN: C1.1, JP1.1, R3.2, R4.2, U2.1 (IN), U2.3 (EN)
XSHUT: D1.C, JP1.5
XSHUT_2.8V: D1.A, R5.1, U1.5 (XSHUT)

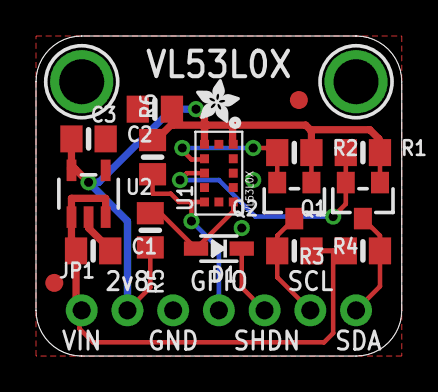
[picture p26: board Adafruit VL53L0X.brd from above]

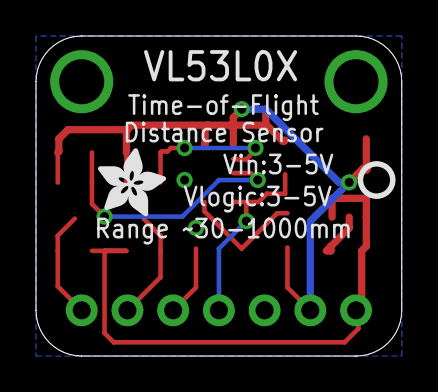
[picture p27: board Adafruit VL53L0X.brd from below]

Board: 2 copper layers, 20.3 x 17.8 mm, 22 parts (2 on the bottom side), 10 nets.

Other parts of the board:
U$12: PCBFEAT-REV-040
U$15: ADAFRUIT_3.5MM
U$18: ADAFRUIT_2.5MM

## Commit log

2017-07-20 Adding docs
    [PCB design rules.xlsx, PCB sellers.xlsx, ProjectPlan.xlsx]
2017-07-20 More docs
    [TI_battery.sch]
2017-07-20 3D model and some other files
    [Adafruit VL53L0X.brd, Adafruit VL53L0X.sch, CamPrj.skp, CamPrj_alt_1.skp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]
2017-07-20 Adding KiCAD PCB project
    [IMU.sch, LED_Drive.sch, RPI_pinout.sch, TI_battery.sch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]
2017-07-23 Board design: component placement done
    [IMU.sch, LED_Cordniates.xlsx, LED_Drive.sch, RPI_pinout.sch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]
2017-07-27 routing done
    [PCB design rules[english].xlsx, PCB manufacturers[english].xlsx, ProjectPlan.xlsx, camprj_kicad.kicad_pcb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]
2017-08-02 Final Delivery
    [IMU.sch, RPI_pinout.sch, camprj_kicad-B.Cu.gbl, camprj_kicad-B.Cu.gbr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]
2017-08-03 Logos updated
    [SeedStudio_prices.xlsx, camprj_kicad-F.SilkS.gto, vitalCamV2-B.Cu.gbl, vitalCamV2-B.Mask.gbs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]
2017-08-03 fixing pathnames
    [SeedStudio_prices.xlsx, vitalCamV2-B.Cu.gbl, vitalCamV2-B.Mask.gbs, vitalCamV2-B.Paste.gbp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]

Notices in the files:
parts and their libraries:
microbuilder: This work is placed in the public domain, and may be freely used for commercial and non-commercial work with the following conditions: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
